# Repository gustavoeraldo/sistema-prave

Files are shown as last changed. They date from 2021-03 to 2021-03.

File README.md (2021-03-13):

# sistema-prave
No projeto de ingressão no Laboratório LAIS da UFRN, cujo o objetivo é auxilar na reabilitação de pacientes vítimas de Acidente Vascular Encefálico (AVE). 

## Índice

<ol align="left">
  <li><a href="#introdução">Introdução</a></li>
  <li><a href="#objetivo">Objetivo</a></li>
  <li><a href="#20-instrumentação-e-modelagem">Instrumentação e modelagem</a>
    <ol>
      <li><a href="#21-estágio-diferencial">Estágio diferencial</a></li>
      <li><a href="#22-estágio-de-filtragem">Estágio de filtragem</a></li>
      <li><a href="#23-estágio-de-amplificação-e-retificação">Estágio de amplificação e retificação</a></li>
    </ol>
  </li>
  <li><a href="#30-interface-gráfica">Interface gráfica</a></li>
  <li><a href="#40-sistema-de-corrida">Sistema de corrida</a></li>
  <li><a href="#50-lista-de-materiais">Lista de materiais</a>
    <ol>
      <li><a href="#51-hardware">Hardware</a></li>
      <li><a href="#52-softwares">Softwares</a></li>
    </ol>
  </li>
  <li><a href="#60-orçamento-do-projeto">Orçamento do projeto</a></li>
  <li><a href="#referências">Referências</a></li>
  <li><a href="#melhorias-e-ideias">Melhorias e ideias</a></li>

</ol>

## 1.0 Introdução
<!-- Falar um pouco sobre a aplicação -->
<!-- Falar a sequência de passos utilizados para desenvolver o projeto -->
<!-- Diagrama de blocos de todo o sistema/projeto (uma visão geral) -->

É apresentada a lista de materiais e serviços necessários para o desenvolvimento da solução proposta. Vale ressaltar que na listagem de materiais encontram-se o hardware e softwares utilizados, juntamente com a justificativa da escolha de cada item. 

Neste projeto a sequência de desenvolvimento foi dada por:

1. Modelagem e simulação do circuito
2. Desenvolvimento da interface gráfica
3. Sistema para controle dos carrinhos para efetuar o funcionamento da corrida

## 2.0 Instrumentação e modelagem
[voltar para o índice](#índice)
<!-- Mostrar cálculos e simulações -->
Para realizar a medição de biopotenciais é necessário realizar uma amplificação do sinal, já que a ordem da resposta elétrica varia entre uV e mV. Na medição de EMG é em torno de 1mV~10mV (Referência: Livro de Instrumentação, pg). 

O circuito desenvolvido é composto por quatro módulos, sendo estes o módulo diferencial, filtragem do sinal, amplificação e retificação do sinal, como é possível observar no diagrama abaixo.

<p align="center">
  
   <p align="center">Figura 1. Diagrama do circuito</p>
</p>

### 2.1 Estágio diferencial
<!-- adicionar mais informações sobre esse circuito e o porquê de utilizá-lo -->
Na construção do circuito que fará a medição de biopotenciais é necessário atentar-se as questões de segurança dos pacientes,    

Para a construção deste estágio foi utilizada a configuração do amplificador de instrumentação, já que este tipo de amplificador diferencial permite:

- Alto ganho para entradas diferenciais é pequenas (mV): fator importante na obtenção das leituras em pacientes que estão em reabilitação, pois talvez tenham uma resposta elétrica muito baixa;
- Grande common mode rejection ratio (CMRR): aumenta a precisão ou ;
- Alta impedância de entrada, evitando o fluxo de altas correntes;

<!-- O GANHO NESSE ESTÁGIO DEVE SER DE 2.2 -->
<p align="center">
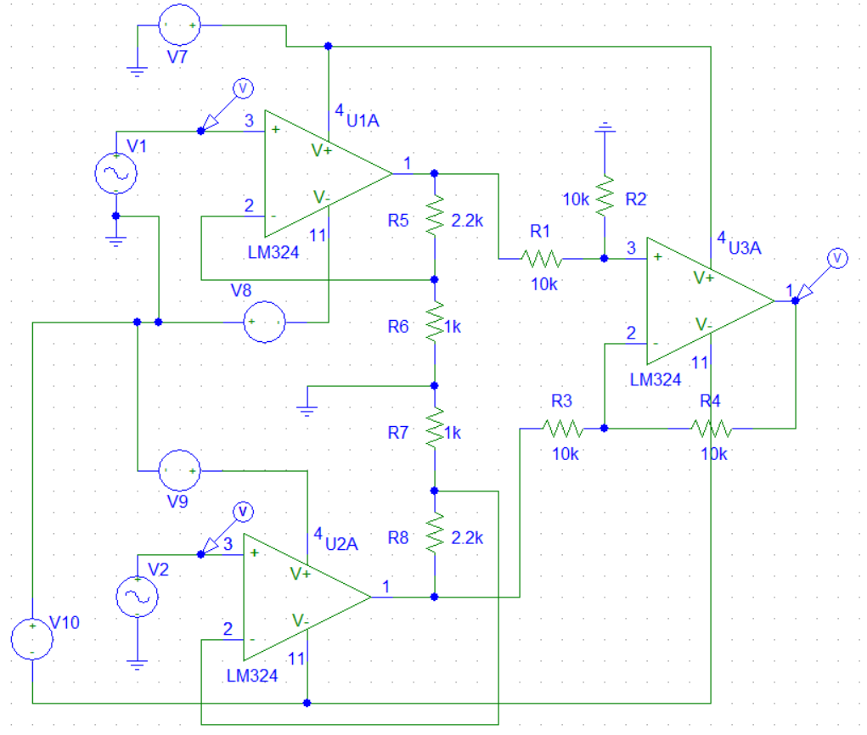
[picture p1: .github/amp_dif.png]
  
   <p align="center">Figura 2. Estágio de pré-amplificação e diferencial</p>
</p>

**Simulação do circuito**

Para caracterizar os impulsos elétricos de entrada do circuito, utilizou-se um sinal senoidal com frequência de 100Hz e amplitude de 10mV e 5mV para V1 e V2 respectivamente, como é possível observar na figura seguinte.

<p align="center">
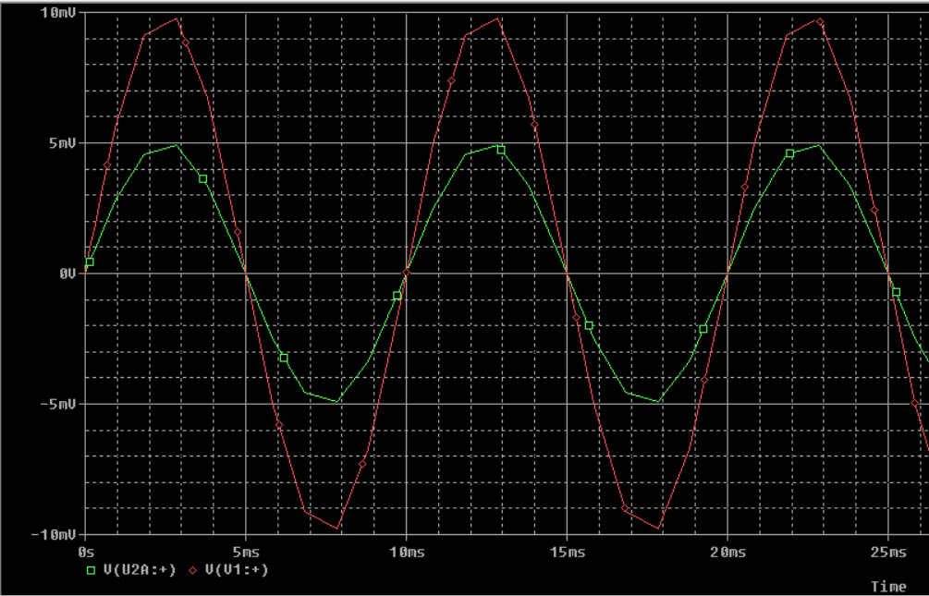
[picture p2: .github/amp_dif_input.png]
  
  <p align="center">Figura 3. Entrada diferencial do circuito</p>
</p>

**Saída do estaǵio diferencial**

Na imagem abaixo observa-se o comportamento esperado, visto que a diferença entre V1 e V2 é de 5mV, e o ganho do estágio de pré-amplificação é de 101, resultando asim uma saída é levemente superior a 500mV. 
<!-- mudar esse ganho -->

<p align="center">
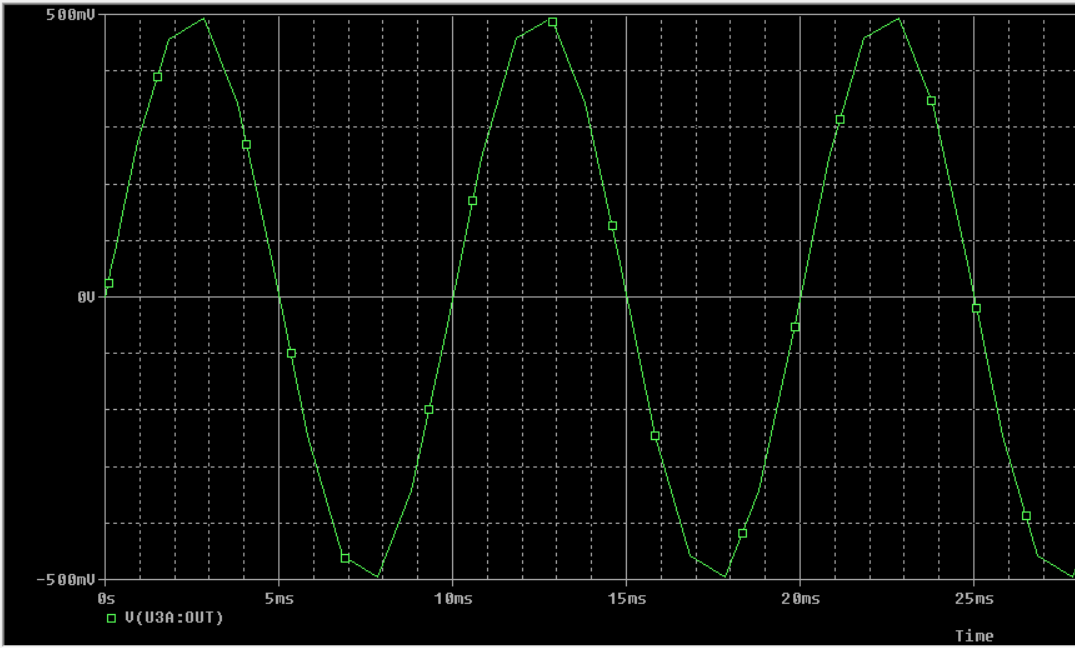
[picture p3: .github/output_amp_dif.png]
  
</p>

**Cálculo**

Como este módulo possui inicialmente um estágio de amplificação com a configuração não inversora, então o ganho deste estágio é representado pela seguinte equação:

```
Av = (R5/R6) + 1 
```
Então, tem-se que:
```
Av = (R5/R6) + 1
# Lembrando que R5 = R8 e R6 = R7
Av = (100k/1k) + 1
Av = 101 

# e Av(CM) = 1
```

Por fim, no estágio do amplificador diferencial, o ganho Av = -1, devido ao casamento de impedância dos resistores R1, R2, R3 e R4. Já o Av(CM) dependerá da precisão dos resistores:

```
Av(CM) = +-2 * (delta_R/R)
```

### 2.2 Estágio de filtragem

Para reduzir a presença de ruídos na aquisição do EMG, foi necessário realizar a construção de um módulo de filtragem. Como os sinais de EMG apresentam frequências entre 20 e 500Hz (Adicionar referências).

Como o objetivo é construir um filtro passa-faixa, dentre as possíveis configurações existentes optou-se por utilizar um passa-altas e passa-baixas em sequência. Isto é um fator facilitador quando a faixa de banda é específica, pois basta projetar a frequência de corte para cada estágio. 

<p align="center">
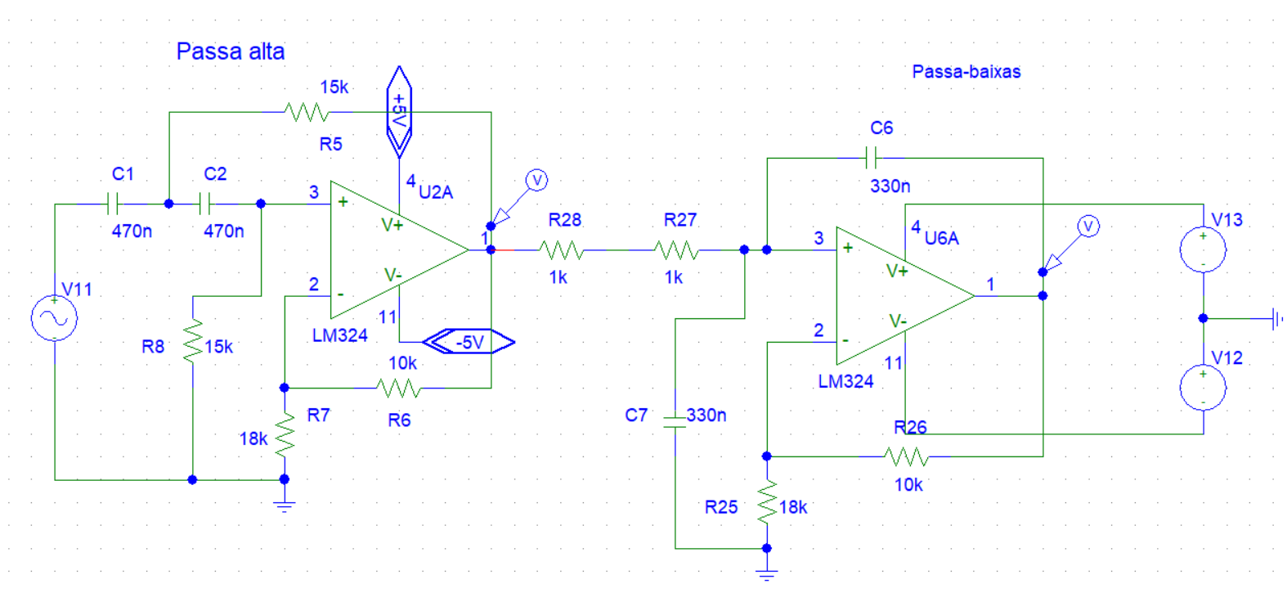
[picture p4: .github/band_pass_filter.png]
  
  <p align="center">Figura 4. Filtro passa-faixa</p>
</p>
<!-- Descrever as características da tensão de entrada
  Mostrar os cálculos
  Colocar referências (OpenHardware)
  [ ] - Mostrar tensão de entrada
 -->

O primeiro estágio deste módulo é um filtro passa-altas Sallen-Key de componentes iguais ([Malvino](#referências), página 826). Essa configuração foi escolhida devido a simplificação na seleção dos valores de cada componente.

<p align="center">
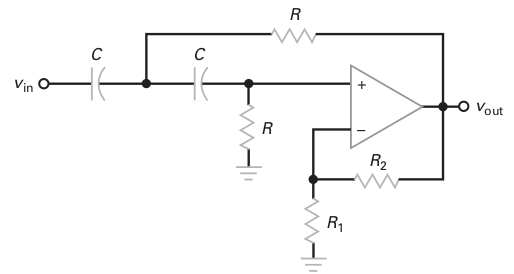
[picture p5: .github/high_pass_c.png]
  
  <p align="center">Figura 5. Filtro passa-altas Sallen-Key (Fonte: <a href="#referências">Malvino</a>, página 827)</p>
</p>

**Modelagem**

O filtro passa-altas precisa ter uma frequência de corte de 20Hz, então a escolha dos componentes partirão a partir da definição de algumas constantes:

* Q: Constante que define a aproximação da frequência de corte. 

* Fp: frequência de polo

* Fc: frequência de corte

* Av: ganho do circuito

* *k*<span style="font-size: 12px; font-style:italic">c</span>: constantes estabelecidas por simplificações realizadas por Butterworth, Bessel e Chebyshev com base na amplitude da ondulação de estágios de segunda ordem ([Malvino](#referências), página 815 vol. 2).

Tendo isto em vista, para facilitar os cálculos, dado que:

```
fc = fp/kc
```

* Deseja-se que *f*<span style="font-size: 12px; font-style:italic">c</span> = *f*<span style="font-size: 12px; font-style:italic">p</span>. Portanto, com base na tabela *k*<span style="font-size: 12px; font-style:italic">c</span> = 1. Entãp *f*<span style="font-size: 12px; font-style:italic">c</span> = *f*<span style="font-size: 12px; font-style:italic">p</span> = 20Hz.

A partir disto pode-se encontrar o resistor **R** e do capacitor **C** pela equação:

```
=> fp = 1/(2*pi*R*C)
=> 20 = 1/(2*pi*R*C)
=> RC = 1/(40*pi)
=> RC = 0.007957747
```

A partir deste momento o valor de R ou C deve ser arbitrário, então escolhendo R = 15k Ohms, tem-se que:

```
=> C = 0.007957747/15k
=> C = 531nF 
```

Então o capacitor será de 470nF, já que é o capacitor comercial mais próximo.
Por fim, para que a condição de *k*<span style="font-size: 12px; font-style:italic">c</span> = 1 seja satisfeita, a constante Q deve estar no intervalo: 0.577 < Q <= 0.707 . O valor de Q é obtido por:

```
Q = 1/(3 - Av)
# Av é obtido por:
Av = (R2/R1) + 1

# Logo: 
=> Av >= -1/0.707 + 3
=> Av = 1.58557

# Assim
R2/R1 = 0.58557
R2 = 0.58557*R1
```

Escolhendo R1 arbitrariamente igual a 18k Ohms, R2 = 10.5k Ohms, logo R2 = 10k Ohms.

**Passa-baixas**

Analogamente para o filtro passa-baixas aprensenta os mesmos passos:

<p align="center">
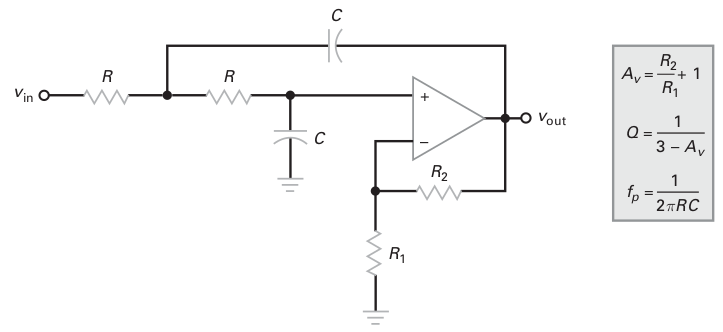
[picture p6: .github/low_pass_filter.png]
  
  <p align="center">Figura 6. Filtro passa-baixas Sallen-Key (Fonte: <a href="#referências">Malvino</a>, página 822)</p>
</p>

**Simulação**

Na imagem abaixo é apresentado a saída do filtro passa-altas e passa-baixas caracterizados pela senoidal vermerlha e verde respectivamente. Certamente o sinal no final do estágio tem amplitude levemente maior devido ao ganho de 1.5 aproximadamente. Além disso o sinal não sofre deformações dentro da faixa de operação estabelecida.

<p align="center">
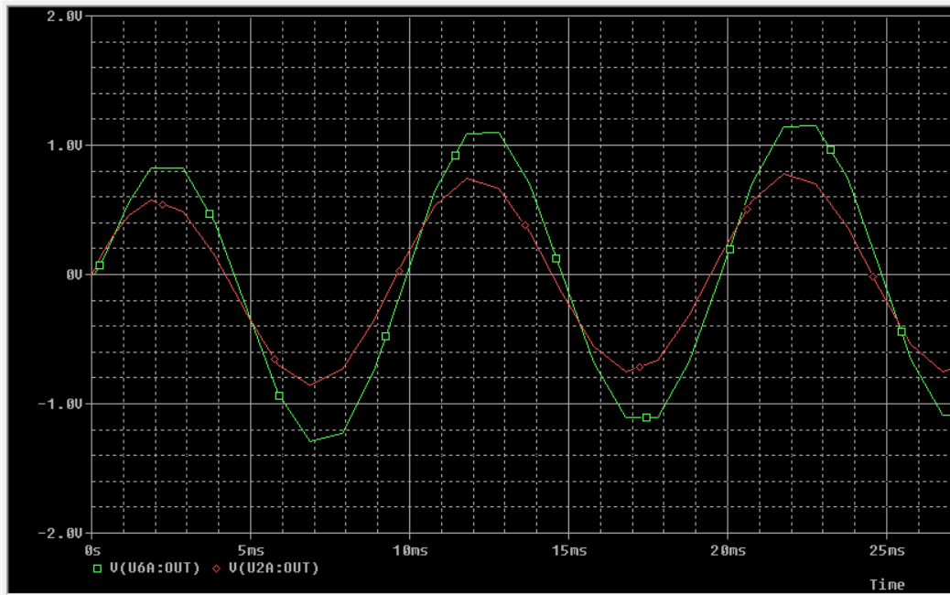
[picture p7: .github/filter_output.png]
  
</p>

### 2.3 Estágio de amplificação e retificação

Neste estágio realiza-se a amplificação final do sinal juntamente com a retificação deste, visto que o sinal será convertido para um sinal digital. Além disso, este estágio permite ajuste do ganho, tendo então um valor entre 47 e 147 proximadamente concretizando um ganho máximo de 750 ou 57.2 db.

**Modelagem**

Para obter o ganho descrido anteriormente, basta ecolher arbitrariamente um dos resistores R1 ou R2. Lembrando que R2 = R2' + R3.

```
Av = R2/R1 + 1
```

Partindo de Av(total) = 750, porém com os estágios anteriores apresentam um total de 5.1, pois:

```
2.2 * ~1.5 * ~1.5 = 5.1

# então Av no último estágio deve ser de:
=> Av = 750/5.1
=> Av = 147
```

Por fim, calcula-se R2: 

```
=> R2 = (147-1)*1k
=> R2 = 146k Ohms
```
Por fim utilizando um potenciômetro de 100k Ohms e um resistor de 47k Ohms , é obtido um valor próximo ao desejado.

<p align="center">
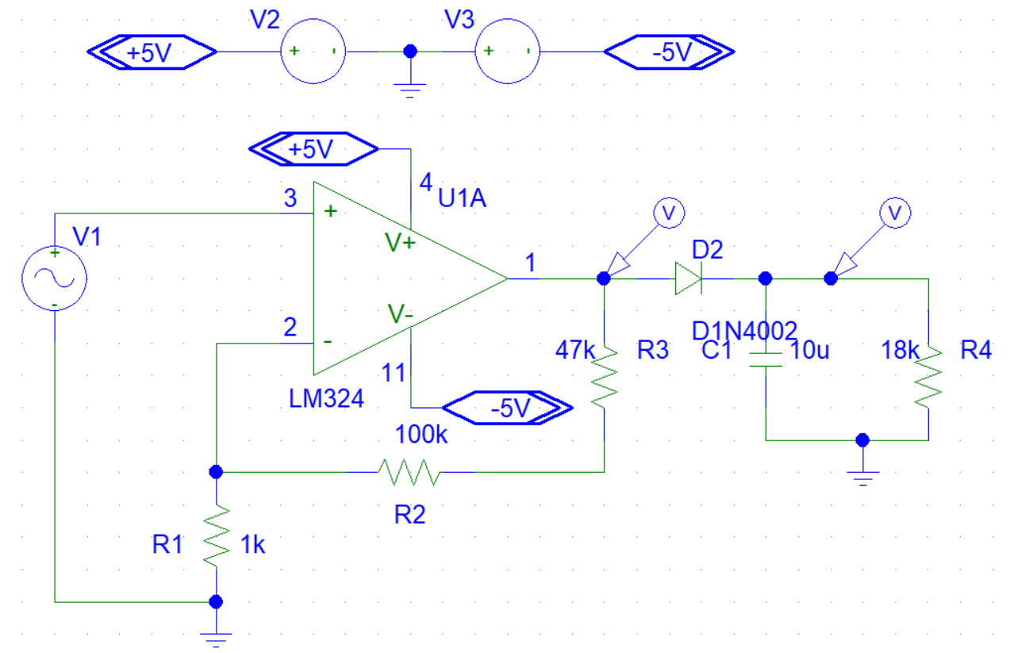
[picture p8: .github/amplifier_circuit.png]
  
  <p align="center">Figura 7. Estágio final de amplificação e retificação do sinal</p>
</p>

**Retificação**

Por fim, o circuito apresenta um estágio de retificação do sinal como um fitlro de onda completa: 

<p align="center">
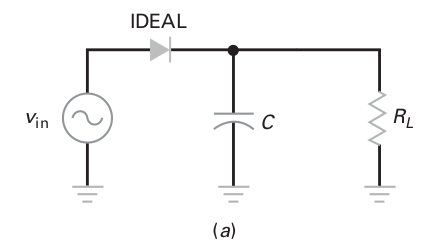
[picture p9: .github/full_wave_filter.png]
  
  <p align="center">Figura 8. Filtro de onda completa (Fonte: <a>Malvino</a>, página 105 vol. 1)</p>
</p>

```
Vr = I/fC

# onde
Vr = ondulação de pico a pico
I = corrente CC na carga
f = frequência da ondulação
C = capacitância
```

**Simulação**

Na figura abaixo é apresentado a saída do estágio de amplificação juntamente com a retificação da senoide.

<p align="center">
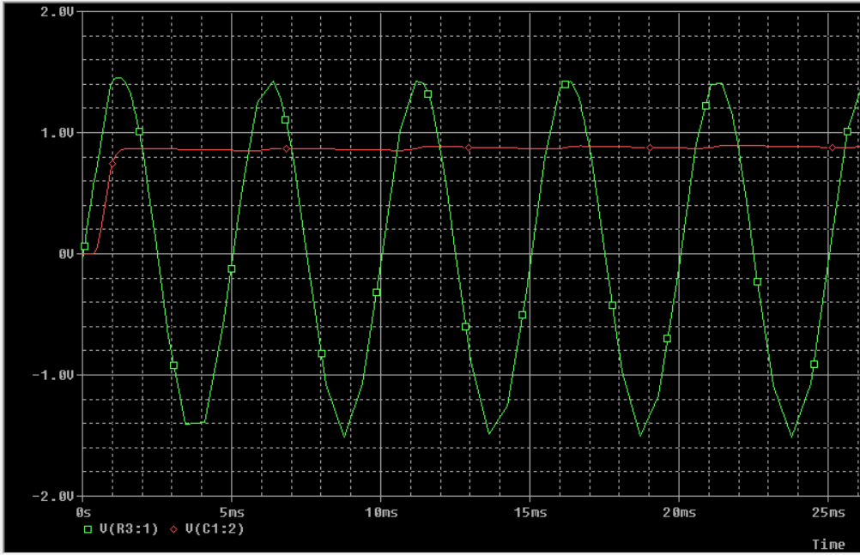
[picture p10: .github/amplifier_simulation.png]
  
  <p align="center">Figura 9. Simulação do circuito de amplificação</p>
</p>

## 3.0 Interface gráfica 
[voltar para o índice](#índice)

Uma vez que a visualização gráfica é necessária para o profissional de saúde que fará o acompanhamento do paciente, foi desenvolvida uma interface gráfica que permite a visualização em tempo real da resposta muscular do paciente. Além disso, o usuário poderá fazer a exportação de um arquivo .CSV com os dados armazenados da consulta.

A interface recebe informações enviadas pelo arduino uno via comunicação serial. Para fins de simulação foi realizada a variação de tensão sob um potenciômetro de 10k Ohms, assim foi validado o funcionamento da interface.

A interface foi desenvolvida utilizando a ferramenta [Qt](https://www.qt.io/) e os motivos que levaram a escolha deste software estão descritas na seção de [Lista de Materiais](#Software). 

<p align="center">
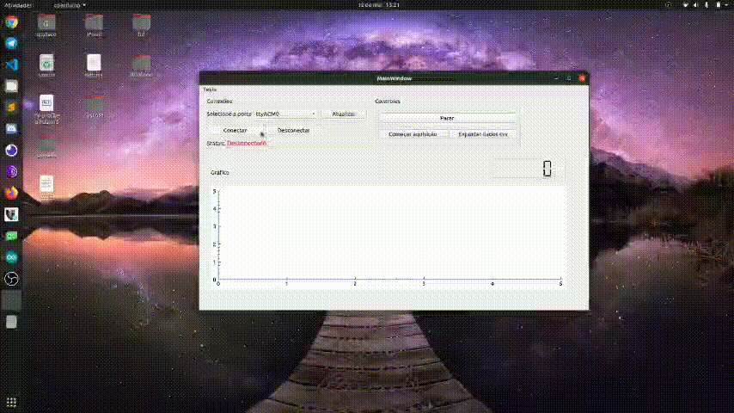
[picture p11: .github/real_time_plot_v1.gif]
  
</p>

## 4.0 Sistema de corrida
[voltar para o índice](#índice)

Para esta primeira versão do sistema desenvolvido neste projeto, tem-se suporte para apenas 1 jogador, já que na especificação indica que o sistema deve possuir até 4 jogadores. Entretando, esta limitação pode ser removida com melhorias futuras. Outro ponto importante é que priorizou-se utilizar materiais de fácil acesso, de modo que fosse possível reaproveitar materiais recicláveis.

Foi utilizado um arduino uno para simular o controlador do sistema e um motor DC responsável por tracionar o carro de brinquedo. O [controle](./car_controller/car_controller.ino) desenvolvido para a ativação do motor é simples, a velocidade será proporcional a tensão lida pelo arduino. O arduino uno possui 10 bits de resolução, então os valores são convertidos entre 0 e 1023. Já a velocidade do motor DC é controlada por meio de um pulso PWM, cujo o duty cycle varia de 0 a 255, representando 0 a 100%.  

<p align="center">
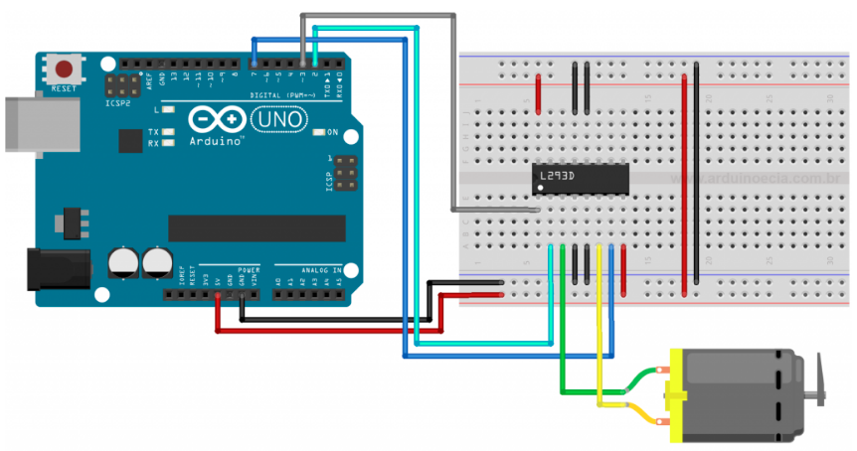
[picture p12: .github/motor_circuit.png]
  
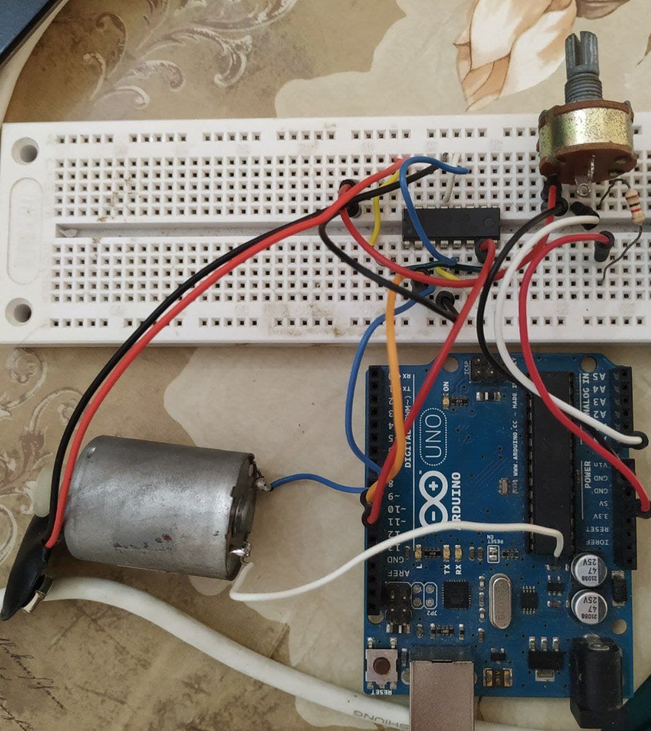
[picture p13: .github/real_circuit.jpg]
  
  <br>
  <p align="center">Figura 10. Circuito para controle do motor: esquemático e testado (Fonte: <a href="https://www.arduinoecia.com.br/controle-de-motor-dc-com-o-l293d-ponte-h/">Arduino e Cia</a>).</p>
</p>
<br>

Já em relação ao ambiente/pista de corrida, optou-se por utilizar uma impressora, como pode-se observar na figura abaixo. A motivação da escolha parte da ideia de reciclagem, além disso a mecânica da estrutura permite a mesma dinâmica propocionada por jogos *drag racing*. Em paralelo ao motor tem-se um sensor ultra sônico para frenagem do carrinho quando este se aproximar na "linha de chegada".
Por fim o carro de brinquedo é anexado na superfície que é controlada pelo motor. 

<p align="center">
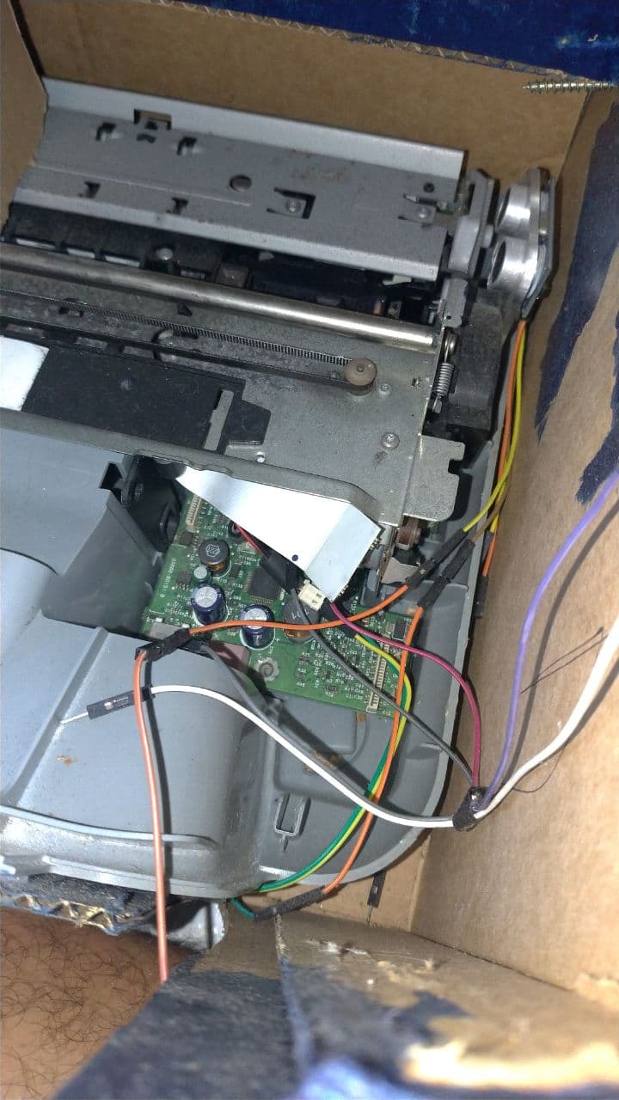
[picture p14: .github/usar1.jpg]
  
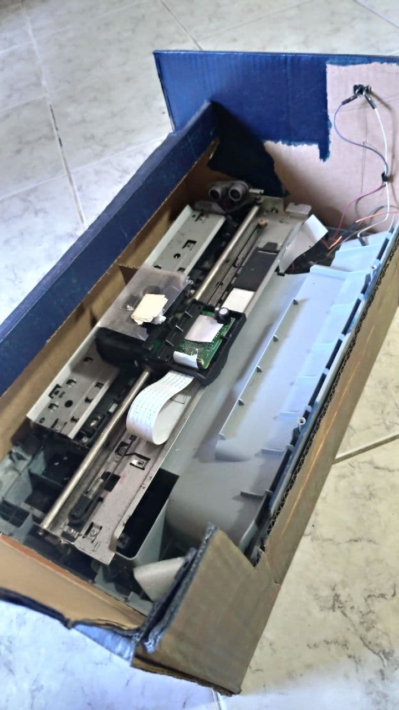
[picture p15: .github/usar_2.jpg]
  
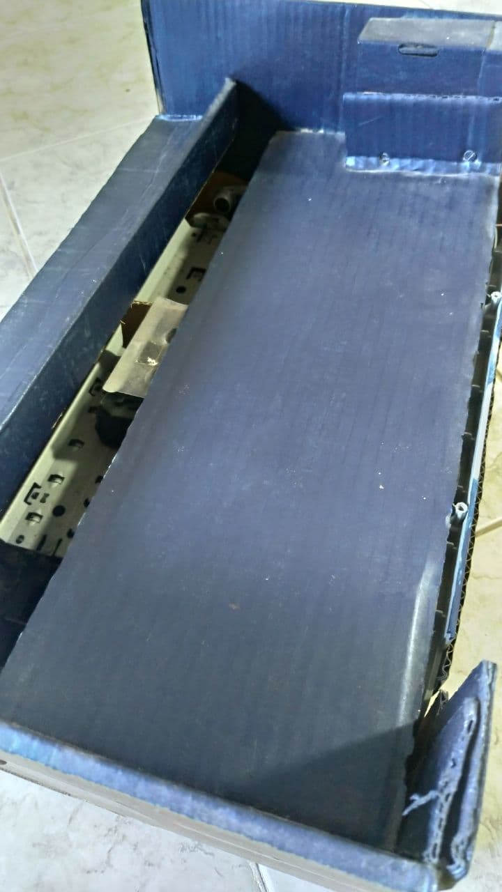
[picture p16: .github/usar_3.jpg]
  
  <br>
  <p align="center">Figura 11. Estrutura da pista</p>
</p>

É importante destacar que esta abordagem via corrida de carrinho é uma forma interessante de analisar o quadro de evolução do paciente. 

## 5.0 Lista de Materiais
[voltar para o índice](#índice)

### 5.1 Hardware

* Operacional [LM324](https://www.alldatasheet.com/datasheet-pdf/pdf/17871/PHILIPS/LM324.html) - 2 unidades (uma unidade contem 4 operacionais);
* Resistores:
	* 1k - 5 unidades;
	* 2.2k - 2 unidades;
	* 10k - 6 unidades;
  * 15k - 2 unidades;
  * 18k - 3 unidades;
	* 47k - 1 unidade;
  * potenciômetro 100k - 1 unidade; 
* Capacitores:
  * 470n - 2 unidades;
  * 330n - 2 unidades;
  * 10u - 1 unidade.
* [Arduino uno]() - 1 unidade;
* [Eletrodo Meditrace]() - 1 unidade:
<!-- Justificar a escolha do eletródo, usar como base o livro de instrumentação -->
* [Max1044/icl7660](https://datasheets.maximintegrated.com/en/ds/ICL7660-MAX1044.pdf): um conversor de tensão para -5V, este componente simplificará o circuito final para a alimentação simétrica dos estágios com amplificadores.

* Diodo [1N4007](https://www.diodes.com/assets/Datasheets/ds28002.pdf) : 
 <!-- razão de ter escolhido este diodo  -->

* [L293D](https://www.ti.com/product/L293D?utm_source=google&utm_medium=cpc&utm_campaign=asc-null-null-GPN_EN-cpc-pf-google-wwe&utm_content=L293D&ds_k=L293D+Datasheet&DCM=yes&gclid=Cj0KCQiAv6yCBhCLARIsABqJTjbyCSp6-9STZiHve97iKkTxSuu7bJGU-j3YTwGlzCH-22Rzt1smqeUaAlaZEALw_wcB&gclsrc=aw.ds): é o módulo da ponte H, necessária para controle do motor DC.

* Bateria 9V: 

* Impressora usada.

### 5.2 Softwares
[voltar para índice](#índice) 

* [PSpice](https://www.electronics-lab.com/downloads/circutedesignsimulation/?page=5). Neste projeto foi utilizado este software de simulação por ser gratuito, utilizado em meio acadêmico, disponível para estudantes e devido a familiariadade do projetista com a ferramenta. Embora este software seja uma ótima ferramenta de simulação, a versão para estudante apresenta limitações na complexidade do circuito, então é importante destacar que **as simulações foram realizadas separadamente para cara bloco ou módulo do circuito proposto.**

* [IDE arduino](https://www.arduino.cc/en/software). Software amplamente utilizado para a programação e simulação de microcontroladores. A escolha desta ferramenta se dá devido ao microcontrolador utilizado, neste caso, um arduino uno e além disso devido a todo suporte existente da comunidade.

* [Qt](https://www.qt.io/download-open-source?hsCtaTracking=9f6a2170-a938-42df-a8e2-a9f0b1d6cdce%7C6cb0de4f-9bb5-4778-ab02-bfb62735f3e5). Este sofware foi utilizado para criação da interface gráfica. Por apresentar uma versão open source, ser gratúito, permitir funcionamento em multiplas plataformas e uso da linguagem C++, foram as razões consideradas para utilizar esta ferramenta neste projeto.

## 6.0 Orçamento do projeto
[voltar para o índice](#índice)

Na lista abaixo contém todos os componentes utilizados e o respectivo preço. É importante que os itens da lista são vendidos no Brasil, o valor do orçamento pode ser menor ao comprar os componentes no mercado internacional, porém deve ser levado em consideração a taxa e o tempo de entrega.

* Max1044/icl7660 - R$ [49,90](https://produto.mercadolivre.com.br/MLB-1743219833-max1044icl7660-switched-capacitor-voltage-converters-5-pcs-_JM#position=5&type=item&tracking_id=fe80bb47-8e29-429a-8a61-f6f3be3a011d) (pelo mercado livre)

* LM324 x 2 - R$ [1,03](https://www.baudaeletronica.com.br/amplificador-operacional-lm324n.html?gclid=Cj0KCQiAv6yCBhCLARIsABqJTjaj0-cOeFcvMY6wGXRT5CoDXeGQX5tLPz7QADpjgCrUA2g8Gtalu8UaAli-EALw_wcB)

* Resistores - [14,99](https://produto.mercadolivre.com.br/MLB-1015532232-resistores-com-100-pecas-varios-valores-_JM?matt_tool=87716990&matt_word=&matt_source=google&matt_campaign_id=12413740998&matt_ad_group_id=119070072438&matt_match_type=&matt_network=g&matt_device=c&matt_creative=500702333978&matt_keyword=&matt_ad_position=&matt_ad_type=pla&matt_merchant_id=109997376&matt_product_id=MLB1015532232&matt_product_partition_id=337120033364&matt_target_id=aud-1008379684294:pla-337120033364&gclid=Cj0KCQiAv6yCBhCLARIsABqJTjY92DUYH9Fyz1OgKlSPeCkF38TxOKKuTOIUZQomYxKCjiyug7MAOjcaAs8aEALw_wcB)

* Capacitores - 470n [0,57](https://www.baudaeletronica.com.br/capacitor-de-poliester-470nf-400v.html?gclid=Cj0KCQiAv6yCBhCLARIsABqJTjaj7CKKnigx-DDuqbGECnRDn77l3eBzRDHO9oIkKaxV-wxW_iELqyYaArD1EALw_wcB) + 330n [0,66](https://www.baudaeletronica.com.br/capacitor-de-poliester-330nf-400v.html) + 10u [0,11](https://www.baudaeletronica.com.br/capacitor-eletrolitico-10uf-50v.html)

* Diodo - [0,10](https://www.baudaeletronica.com.br/diodo-1n4007.html?gclid=Cj0KCQiAv6yCBhCLARIsABqJTjYCDgML_hwNaYuIrFaIloHfjzkp_tsy6-y5wSCcHSUoQ8jZdiYpPcAaAk6IEALw_wcB)

* Arduino uno - RS [36,90](https://produto.mercadolivre.com.br/MLB-1685850335-arduino-uno-r3-atmega-328-smd-brinde-cabo-usb-controlador-_JM?matt_tool=87716990&matt_word=&matt_source=google&matt_campaign_id=12413740998&matt_ad_group_id=119070072438&matt_match_type=&matt_network=g&matt_device=c&matt_creative=500702333978&matt_keyword=&matt_ad_position=&matt_ad_type=pla&matt_merchant_id=269651381&matt_product_id=MLB1685850335&matt_product_partition_id=337120033364&matt_target_id=pla-337120033364&gclid=Cj0KCQiAv6yCBhCLARIsABqJTjarAGW08AR7X66GFX_795KQkRx6gDPH78xPzrcPMloh0N7xLmAlg5saAswKEALw_wcB)

* Eletrodo Meditrace - RS [41,18](https://magazinemedica.com.br/produtos/visualiza/sku/344/?gclid=Cj0KCQiAv6yCBhCLARIsABqJTjZzoRbHy1WAj9c4vSvnUQDQzgI5Ux4wIBV78mJrWdSXd9HFd33lOBwaAvqNEALw_wcB)

* L293D - R$ [9,90](https://www.eletrogate.com/ci-l293d-ponte-h-dupla?utm_source=Site&utm_medium=GoogleMerchant&utm_campaign=GoogleMerchant&gclid=Cj0KCQiAv6yCBhCLARIsABqJTjZDDQ6rq1UEFUlfdHNBv94UQoLr0GOK0efWcb2YcgKpTYjtdMOl3mkaAtJOEALw_wcB)

* potenciômetro - R$ [1,85](https://www.baudaeletronica.com.br/trimpot-3296x-25-voltas-de-100k-100-000.html)

Assim totaliza-se um **orçamento** de **R$ 144,46**.

Vale lembrar que pode ter alterações nos valores, já que a pesquisa foi realizada no dia 12 de março de 2021. Além disso não constado o preço da construção da placa.
A impressora também não entrou no valor, pois na solução proposta parte da reutilização de impressoras usadas.

## Referências 
[voltar para o índice](#índice)

[1](#) WEBSTER, H. E. J. G.Measurement, Instrumentation, and Sensors Handbook:Electromagnetic, Optical, Radiation, Chemical, and Biomedical Measurement. 2. ed.[S.l.]: CRC Press, 2014. 1921 p. ISBN 1439848912.<br>

[2](#) Malvino, Albert Paul; e Bates, David J.; Eletrônica, vol. 1 e vol. 2, 8a ed., Ed. McGraw Hill-Bookman, São Paulo, SP, 2016. Também em recurso eletrônico.

## Melhorias e ideias
[voltar para o índice](#índice)

O projeto é bastante interessante, porém a forma do tratamento ou o jogo em questão proposto poderia ser diferente. [Estudos](https://www.sciencedirect.com/science/article/abs/pii/S1052305718303483?casa_token=R-97Jx682GgAAAAA:IZnYHXFlh8e_eh3uZW-UL4i_5VHIjT2pTD1tI1RbCMPusfvjElP92P3CH62AZ4vg9er7yP-pmKg) mostram que a **música** auxilia no processo de recuperação, então poderia ser feito um jogo como *Guitar Hero* em que o paciente realiza o estímulo muscular de acordo com a melodia, desta forma acredita-se que o desempenho melhorasse.

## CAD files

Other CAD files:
emg_pspice/emg_circut.stl
emg_pspice/emg2.stl

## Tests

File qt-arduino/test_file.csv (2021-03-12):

80 | -9.22333e+09
852 | -9.22333e+09
856 | -9.22333e+09
855 | -9.22333e+09
854 | -9.22333e+09
850 | -9.22333e+09
846 | -9.22333e+09
847 | -9.22333e+09
845 | -9.22333e+09
843 | -9.22333e+09
842 | -9.22333e+09
840 | -9.22333e+09
839 | -9.22333e+09
837 | -9.22333e+09
835 | -9.22333e+09
831 | -9.22333e+09
829 | -9.22333e+09
827 | -9.22333e+09
824 | -9.22333e+09
822 | -9.22333e+09
823 | -9.22333e+09
823 | -9.22333e+09
821 | -9.22333e+09
823 | -9.22333e+09
823 | -9.22333e+09
822 | -9.22333e+09
823 | -9.22333e+09
823 | -9.22333e+09
824 | -9.22333e+09
825 | -9.22333e+09
828 | -9.22333e+09
830 | -9.22333e+09
832 | -9.22333e+09
834 | -9.22333e+09
837 | -9.22333e+09
840 | -9.22333e+09
842 | -9.22333e+09
843 | -9.22333e+09
845 | -9.22333e+09
850 | -9.22333e+09
855 | -9.22333e+09
860 | -9.22333e+09
864 | -9.22333e+09
868 | -9.22333e+09
872 | -9.22333e+09
878 | -9.22333e+09
882 | -9.22333e+09
886 | -9.22333e+09
888 | -9.22333e+09
887 | -9.22333e+09
888 | -9.22333e+09
887 | -9.22333e+09
888 | -9.22333e+09
888 | -9.22333e+09
890 | -9.22333e+09
889 | -9.22333e+09
890 | -9.22333e+09
890 | -9.22333e+09
892 | -9.22333e+09
894 | -9.22333e+09
895 | -9.22333e+09
895 | -9.22333e+09
894 | -9.22333e+09
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

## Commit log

2021-03-12 circuit simulation
    [band_pass_filter.sch, emg2.sch, emg2.stl, emg_circut.sch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]
2021-03-12 amp 1st stage description updated
2021-03-12 amp 2nd stage update
2021-03-12 amp 2nd stage completed
2021-03-12 last stage, missing retification
2021-03-12 interface update
    [test_file.csv]
2021-03-13 doc updade +1
    [emg2.sch, emg_circut.sch, non_inverter_amp_emg.sch]
